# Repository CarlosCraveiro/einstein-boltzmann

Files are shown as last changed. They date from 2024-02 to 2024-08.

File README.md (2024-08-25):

# The Einstein-Boltzmann Board

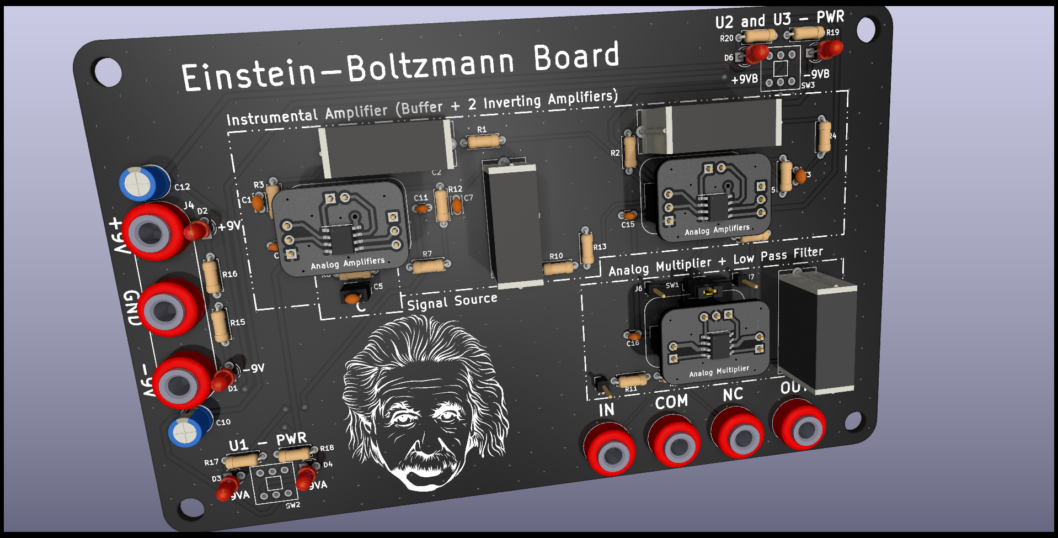
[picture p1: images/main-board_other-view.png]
main_board_other_view


## Project's Intent
Measure the Boltzmann constant through the analysis of the thermal noise of a resistor.

## Disclaimer
This Board was intended to be used with the Guide of the [5-th EPO (2017)](https://github.com/CarlosCraveiro/einstein-boltzmann/tree/main/docs).

So the schematic ideia is not mine, I just adapt and documented it so I could manufacture the board.

The DRC Custom Rules used on this project came from a gist made by [darkxst](https://gist.github.com/darkxst), Gist name: `rules.txt`.

## Project's Dependencies

- KiCAD version 7.0
- KiCAD Addon [kicad-action-scripts](https://github.com/jsreynaud/kicad-action-scripts) (via stitching)

If you use `nix`, to have access to **KiCAD 7.0**, on the project's directory type:

```shell
nix --experimental-features 'nix-command flakes'
nix develop -c $SHELL
```

## Preview Images

### Main Board
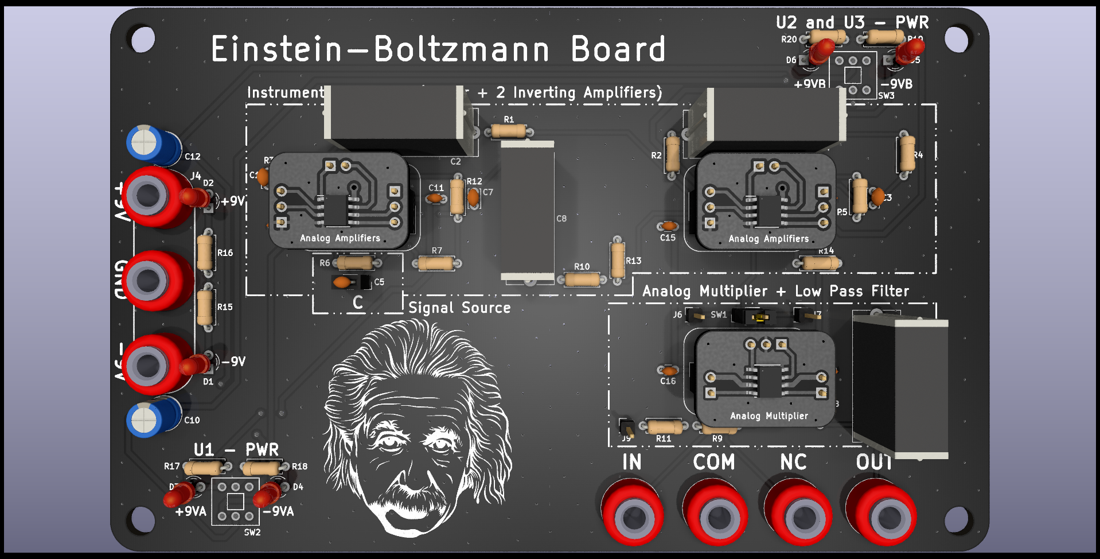
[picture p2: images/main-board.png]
main_board_front

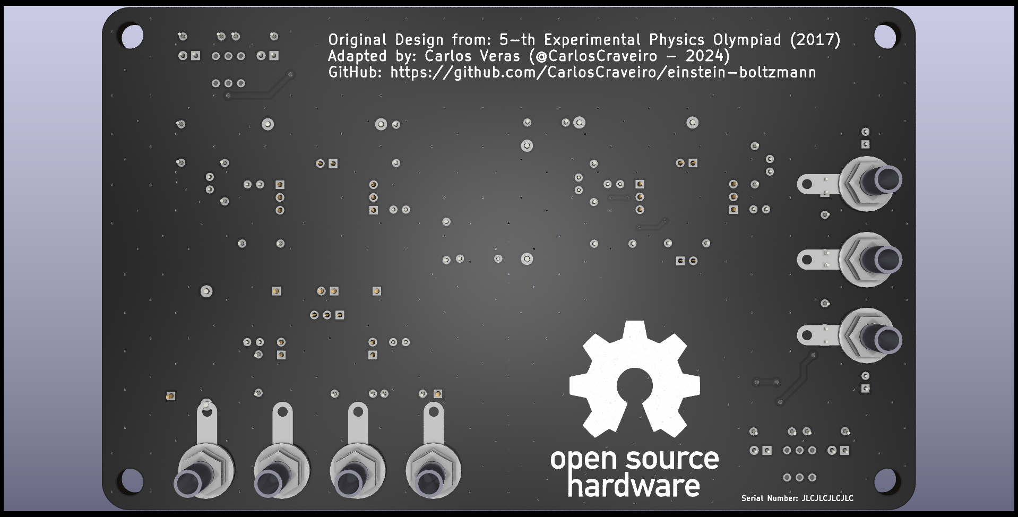
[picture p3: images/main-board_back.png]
main_board_back


### Modules
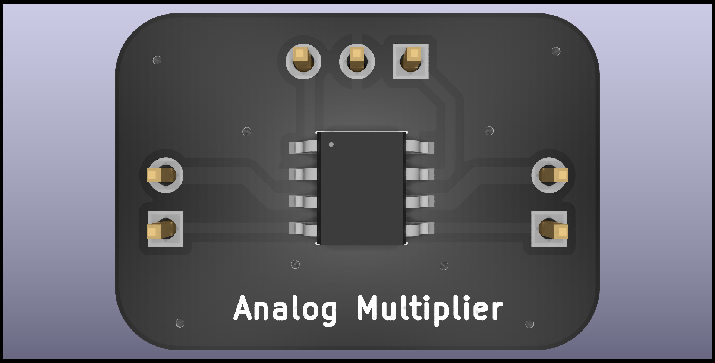
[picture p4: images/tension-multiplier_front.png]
tension-multiplier_front

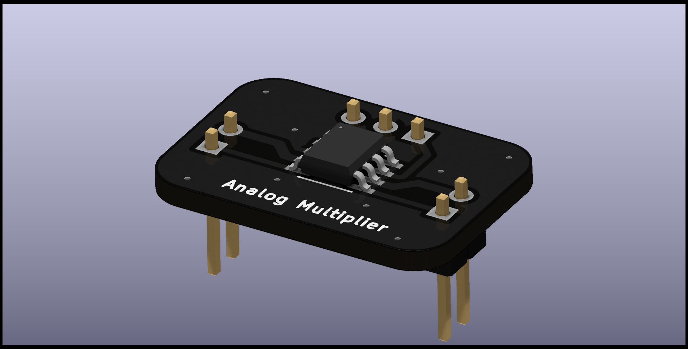
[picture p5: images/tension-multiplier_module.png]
tension-multiplier_module

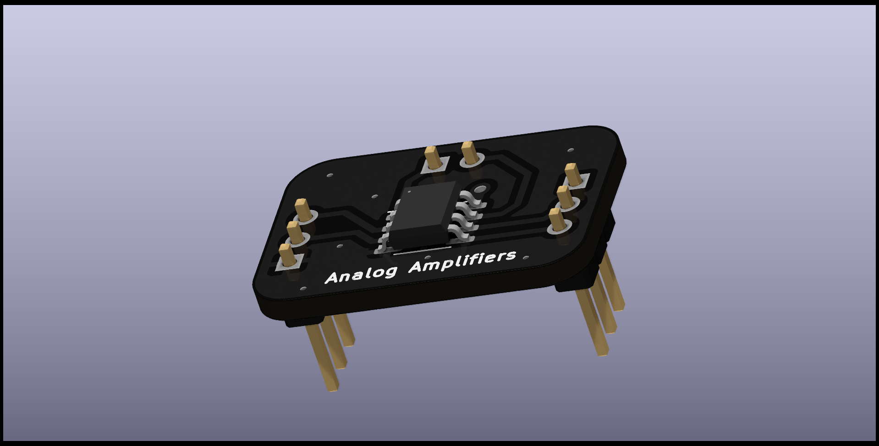
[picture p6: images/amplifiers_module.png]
amplifiers_module

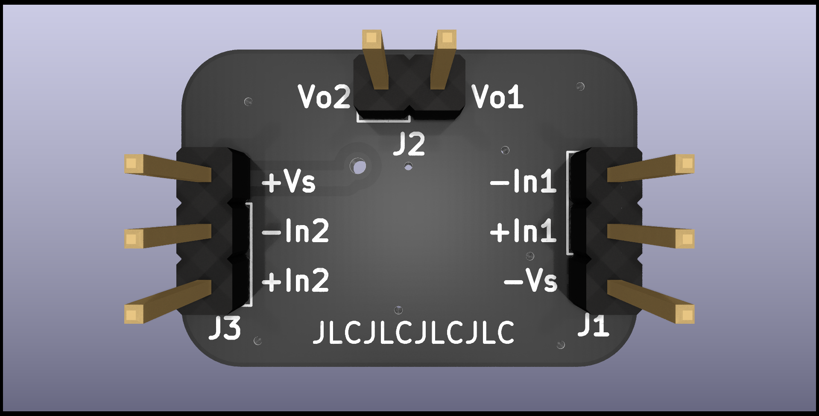
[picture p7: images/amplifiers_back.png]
amplifiers_back


## Real Photos
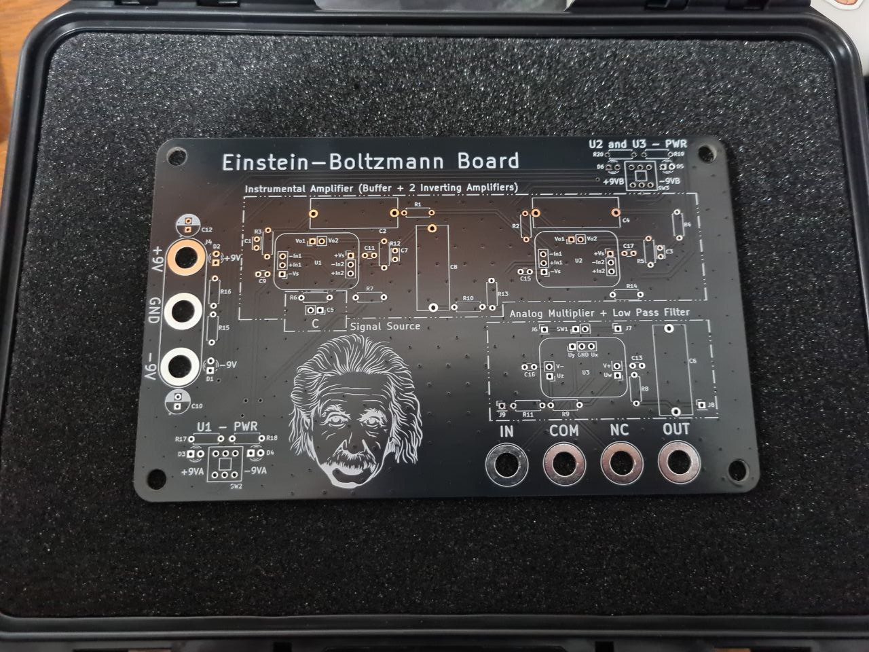
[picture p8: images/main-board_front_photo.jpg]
main-board_front

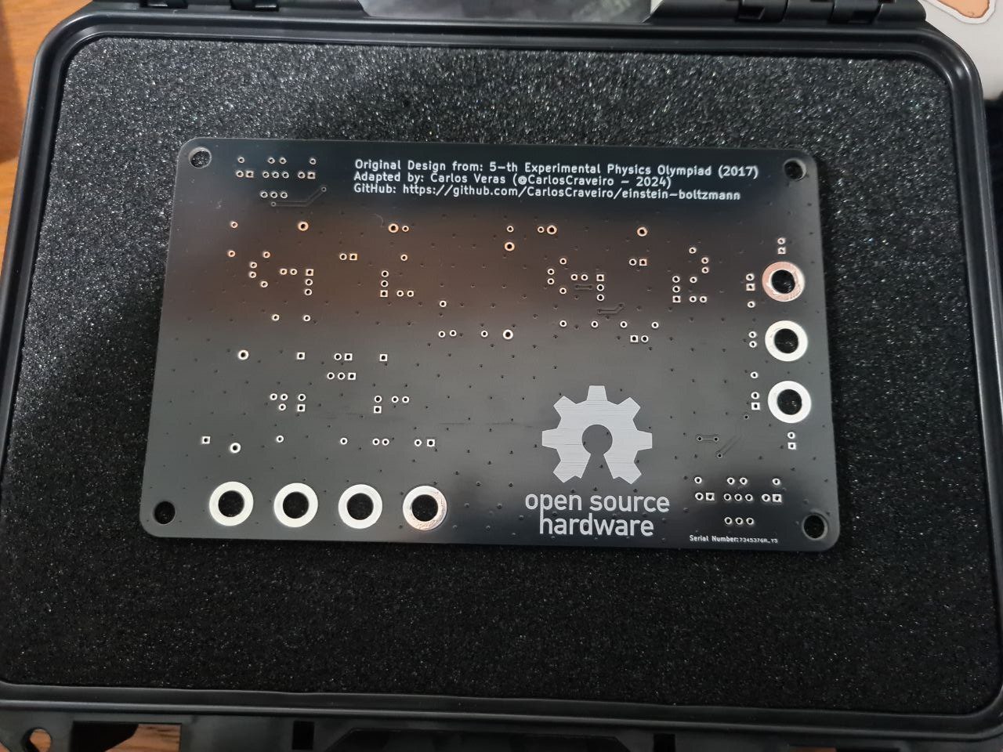
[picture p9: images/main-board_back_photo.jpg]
main-board_back


## TO DO...
- [ ]  Finish soldering the components and modules
- [ ]  Create a Wiki for the project
- [ ]  Measure the Boltzmann constant and publish the results on the project's Wiki
- [ ]  Finish the plate support base (using FreeCAD)
- [ ]  Write a theoretical introduction about the phenomenon on the project's Wiki

*Observation*: I intend to continue working on the project, I just need time.

## Additional information:

I talked about the project at the [FOSFORUMS 2024](https://www.fosforums.org/home) event. The presentation were in English and both the slides and the link for the presentation recording could be access [here](https://github.com/CarlosCraveiro/FOSFORUMS_2024).

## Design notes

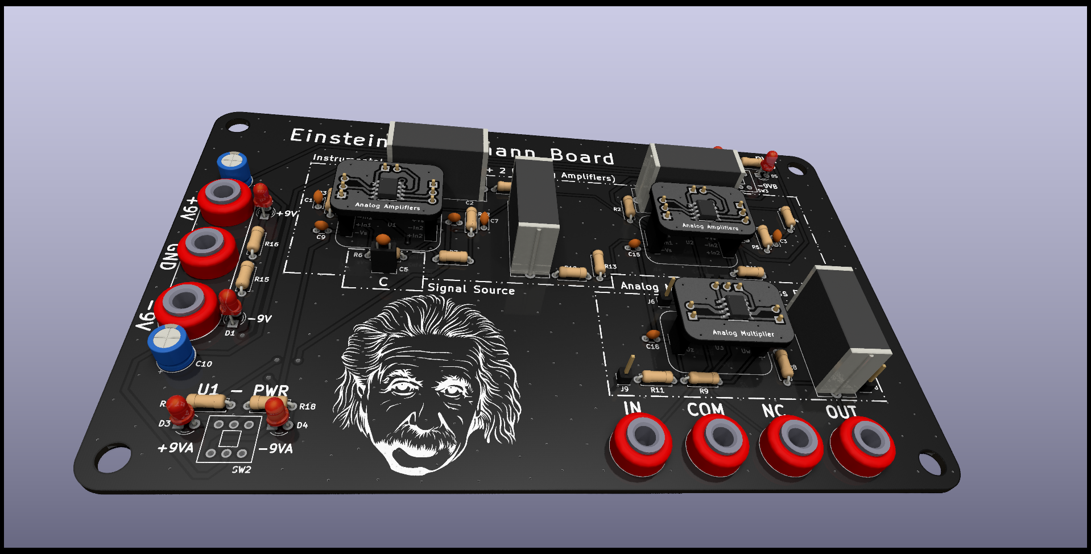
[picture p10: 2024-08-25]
images/main-board_modules_view.png

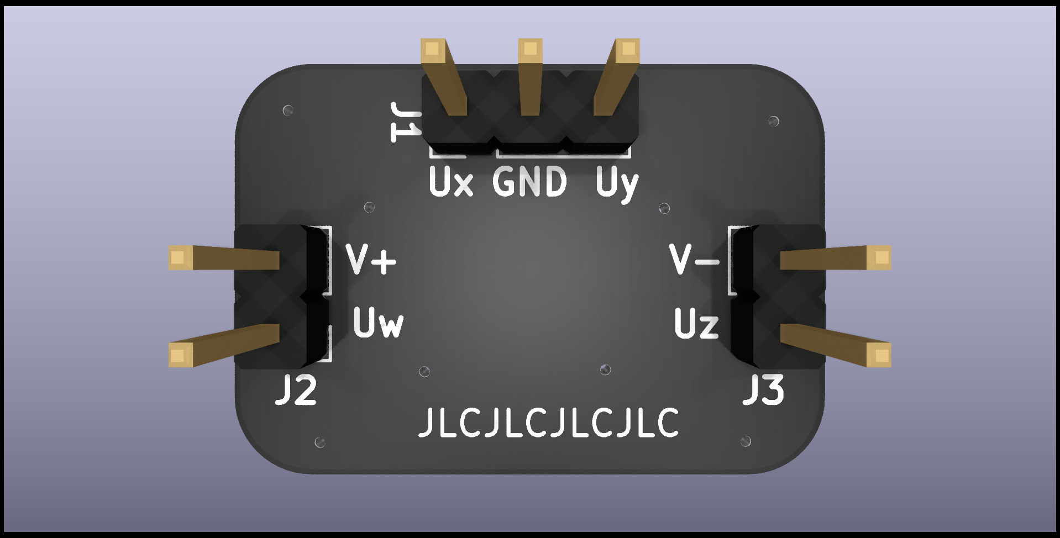
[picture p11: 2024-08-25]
images/tension-multiplier_back.png

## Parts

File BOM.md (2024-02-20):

# BOM - Bill of Materials

## Main Board

|                           |       |
| ------------------------- | ----- |
| Qty of Boards per project | **1** |

* Capacitors: 

| Components               | Qty   |  Unit Price (BRL) | Link                                                                                                      | Link 2 |
| ------------------------ | ----- | ----------------- | --------------------------------------------------------------------------------------------------------- | ------ |
| EC Capacitor 10uF        | **4** | 0.15 / 0.15       | [Bau da Eletronica](https://www.baudaeletronica.com.br/produto/capacitor-eletrolitico-10uf-25v-105c.html) | [Saravati](https://www.saravati.com.br/capacitor-eletrolitico-10uf-16v.html) |
| Tantalum Capacitor 0.1uF | **4** | 0.99              | [Bau da Eletronica](https://www.baudaeletronica.com.br/produto/capacitor-tantalo-01uf-35v.html)           ||
| Tantalum Capacitor 10uF  | **4** | 0.92              | [Bau da Eletronica](https://www.baudaeletronica.com.br/produto/capacitor-tantalo-10uf-16v.html)           ||
| Ceramic Capacitor 10pF   | **3** | 0.17 / 0.10       | [Bau da Eletronica](https://www.baudaeletronica.com.br/produto/capacitor-ceramico-10pf-50v.html)          | [Saravati](https://www.saravati.com.br/capacitor-ceramico-10pf-50v.html) |

* Resistors:

| Components        | Qty   | Unit Price (BRL) | Link                                                                                     | Link 2 |
| ----------------- | ----- | ---------------- | ---------------------------------------------------------------------------------------- | ------ |
| Resistor 510 Ohm  | **1** | 0.05             | [Baú da Eletrônica](https://www.baudaeletronica.com.br/produto/resistor-510r-5-14w.html) | [AliExpress]() |
| Resistor 20 Ohm   | **1** | 0.05 / 0.09      | [Baú da Eletrônica](https://www.baudaeletronica.com.br/produto/resistor-20r-5-14w.html)  | [Saravati](https://www.saravati.com.br/resistor-20r-5-1-4w.html) |
| Resistor 1k Ohm   | **2** | 0.05 / 0.09      | [Baú da Eletrônica](https://www.baudaeletronica.com.br/produto/resistor-1k-5-14w.html)   | [Saravati](https://www.saravati.com.br/resistor-1k-5-1-4w.html) |
| Resistor 100 Ohm  | **4** | 0.04 / 0.09      | [Baú da Eletrônica](https://www.baudaeletronica.com.br/produto/resistor-100r-5-14w.html) | [Saravati](https://www.saravati.com.br/resistor-100r-5-1-4w.html) |
| Resistor 10k Ohm  | **3** | 0.05 / 0.09      | [Baú da Eletrônica](https://www.baudaeletronica.com.br/produto/resistor-10k-5-14w.html)  | [Saravati](https://www.saravati.com.br/resistor-10k-5-1-4w.html) |
| Resistor 1.5M Ohm | **1** | 0.05             | [Baú da Eletrônica](https://www.baudaeletronica.com.br/produto/resistor-1m5-5-14w.html)  | []() |
| Resistor 18k Ohm  | **1** | 0.05             | [Baú da Eletrônica](https://www.baudaeletronica.com.br/produto/resistor-18k-5-14w.html)  | []() |
| Resistor 2k Ohm   | **5** | 0.05             | [Baú da Eletrônica](https://www.baudaeletronica.com.br/produto/resistor-2k-5-14w.html)   | []() |

* LEDs:

| Components | Qty   | Unit Price (BRL) | Link                                                                                     | Link 2 |
| ---------- | ----- | ---------------- | ---------------------------------------------------------------------------------------- | ------ |
| LED 3mm    | **4** | 0.24 / 0.20      | [Bau da Eletronica](https://www.baudaeletronica.com.br/produto/led-difuso-3mm-azul.html) | [Saravati](https://www.saravati.com.br/led-difuso-3mm-azul.html) |

* Pin-Headers:

| Components            | Qty    | Bar Price (BRL) | Link                                                                                               |
| --------------------- | ------ | --------------- | -------------------------------------------------------------------------------------------------- |
| 1x01-P2.54mm_Vertical | **10** | 1.50            | [Saravati](https://www.saravati.com.br/barra-de-pinos-1x40-vias-8-2mm-180-graus-passo-2-54mm.html) |

* Pin-Sockets:

| Components            | Qty   | Bar Price (BRL) | Link                                                                                                |
| --------------------- | ----- | --------------- | --------------------------------------------------------------------------------------------------- |
| 1x03_P2.54mm_Vertical | **5** | 1.90            | [Saravati](https://www.saravati.com.br/soquete-barra-de-pinos-1x40-mci-180-graus-passo-2-54mm.html) |
| 1x02_P2.54mm_Vertical | **4** | 1.90            | [Saravati](https://www.saravati.com.br/soquete-barra-de-pinos-1x40-mci-180-graus-passo-2-54mm.html) |

* Other:

| Components               | Qty   | Unit Price (BRL) | Link                                                                                              | Link 2  |
| ------------------------ | ----- | ---------------- | ------------------------------------------------------------------------------------------------- | ------- |
| Mini-Jumper_1x02_P2.54mm | **1** | 0.15 / 0.15      | [Bau da Eletronica](https://www.baudaeletronica.com.br/produto/conector-mini-jumper-sem-aba.html) | [Saravati](https://www.saravati.com.br/jumper-fecha-contato-preto.html) |

## Analog Amplifiers Board

|                           |       |
| ------------------------- | ----- |
| Qty of Boards per project | **2** |

* Pin-Headers:

| Components            | Qty   |
| --------------------- | ----- |
| 1x03_P2.54mm_Vertical | **2** |
| 1x02_P2.54mm_Vertical | **1** |

* ICs: 

| Components    | Qty   |
| ------------- | ----- |
| ADA4898-2YRDZ | **1** | 

## Analog Multiplier Board

|                           |       |
| ------------------------- | ----- |
| Qty of Boards per project | **1** |

* Pin-Headers:

| Components            | Qty   |
| --------------------- | ----- |
| 1x03_P2.54mm_Vertical | **1** |
| 1x02_P2.54mm_Vertical | **2** |

* ICs: 

| Components | Qty   |
| ---------- | ----- |
| AD633ARZ   | **1** | 

## Experience Components

* Capacitors:

| Components                 | Qty   | Unit Price (BRL) | Link                                                                                             | Link 2    |
| -------------------------- | ----- | ---------------- | ------------------------------------------------------------------------------------------------ | --------- |
| *Ceramic Capacitor 6.8nF*  | **1** | 0.10             | [Saravati](https://www.saravati.com.br/capacitor-ceramico-6-8nf-50v.html)                        |           |
| *Ceramic Capacitor 10.3nF* | **1** | 0.10             | [Saravati](https://www.saravati.com.br/capacitor-ceramico-10nf-50v.html)                         |           |
| Ceramic Capacitor 14.8nF   | **1** | 0.10 / 0.10      | [Baú da Eletrônica](https://www.baudaeletronica.com.br/produto/capacitor-ceramico-15nf-50v.html) | [Saravati](https://www.saravati.com.br/capacitor-ceramico-15nf-50v.html) |
| *Ceramic Capacitor 20.3nF* | **1** | 0.58             | [Baú da Eletrônica](https://www.baudaeletronica.com.br/produto/capacitor-ceramico-20nf-50v.html) |           |
| *Ceramic Capacitor 22.3nF* | **1** | 0.10             | [Saravati](https://www.saravati.com.br/capacitor-ceramico-22nf-50v.html)                         |           |
| Ceramic Capacitor 27.9nF   | **1** | 0.55             | [CaAndMa](https://caandma.com.br/)                                                               |           |
| Ceramic Capacitor 33.4nF   | **1** | 0.14 / 0.10      | [Baú da Eletrônica](https://www.baudaeletronica.com.br/produto/capacitor-ceramico-33nf-50v.html) | [Saravati](https://www.saravati.com.br/capacitor-ceramico-15nf-50v.html) |
| Ceramic Capacitor 42.3nF   | **1** | 0.10             | [Saravati](https://www.saravati.com.br/capacitor-ceramico-47nf-50v.html)                         |           |
| Ceramic Capacitor 66.9nF   | **1** | 0.10             | [Saravati](https://www.saravati.com.br/capacitor-ceramico-68nf-50v.html)                         |           |
| Ceramic Capacitor 105nF    | **1** | 0.10             | [Saravati](https://www.saravati.com.br/capacitor-ceramico-100nf-50v.html)                        |           |

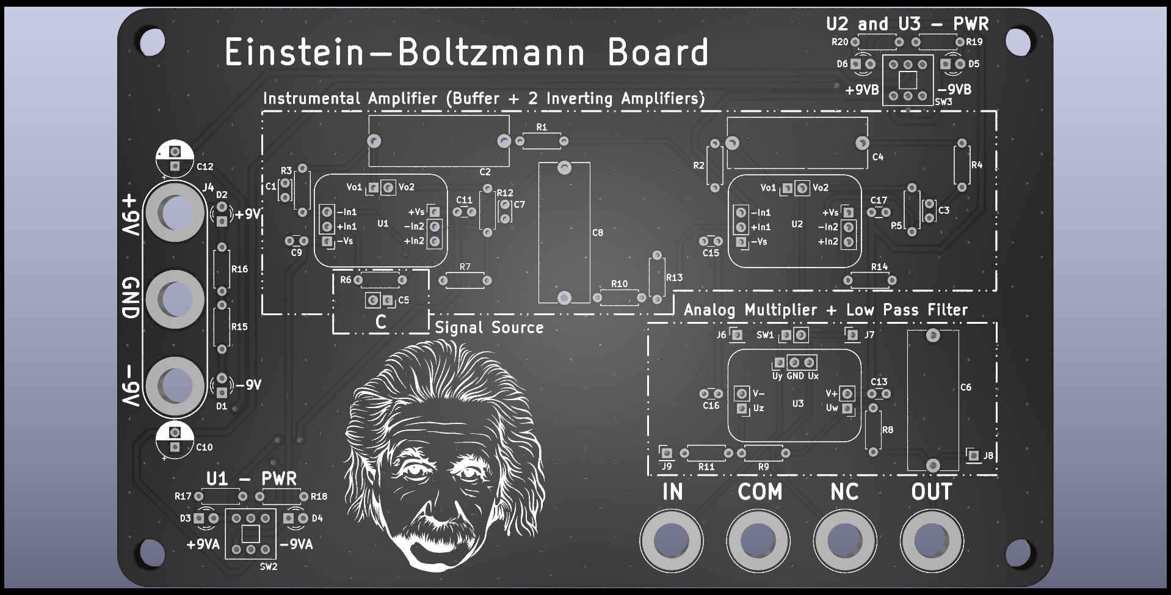
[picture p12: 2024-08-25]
images/main-board_front_no_components.png

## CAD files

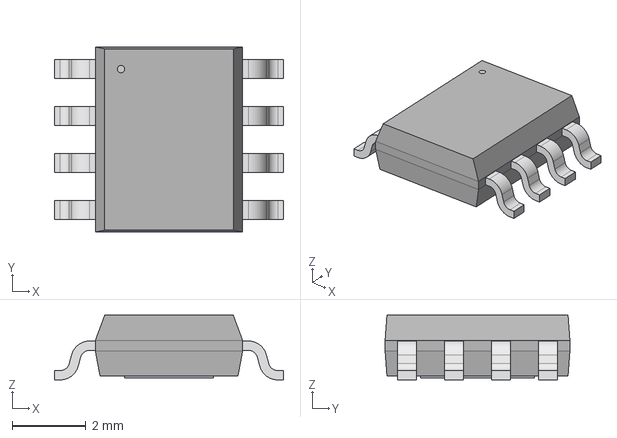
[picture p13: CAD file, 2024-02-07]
amplifiers/RD_8_2_ADI.step
6.20 x 5.00 x 1.75 mm

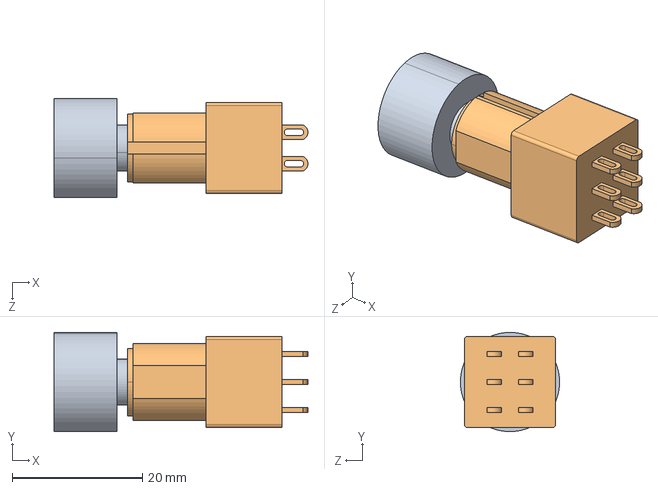
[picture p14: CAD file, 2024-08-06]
main-board/module_3Dmodels/DPDT.step
39.0 x 15.2 x 15.2 mm
MPG206R(2)
MPG206R(1)

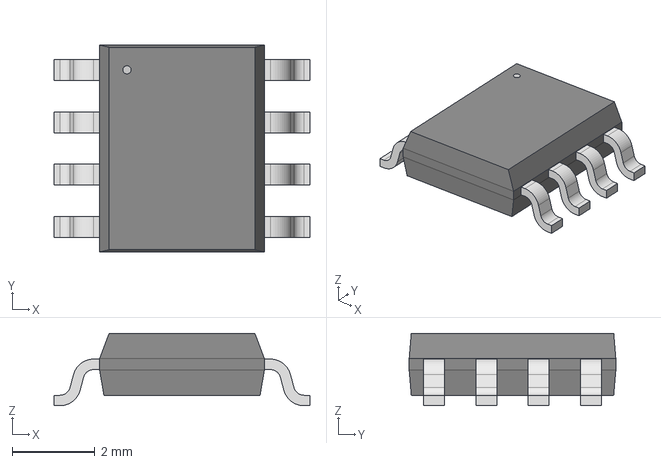
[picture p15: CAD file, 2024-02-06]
tension-multiplier/R_8_ADI.step
6.20 x 5.00 x 1.75 mm

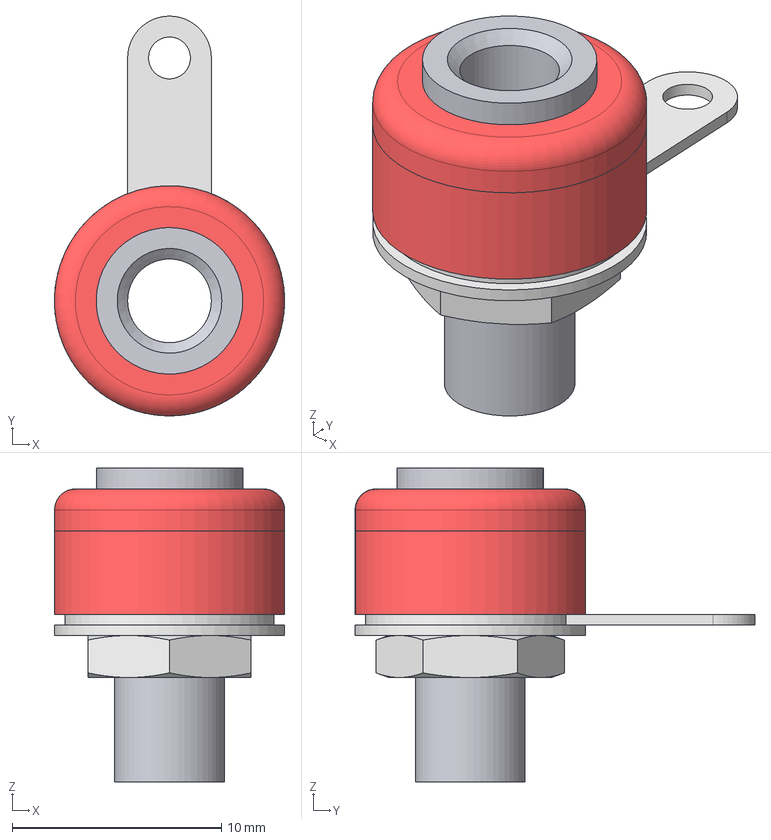
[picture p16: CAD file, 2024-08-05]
main-board/module_3Dmodels/4mm Panel Mount Banana Socket.stp
11.0 x 19.1 x 15.0 mm
Plastic Cap
Plastic Cap top
Socket Tube
Wire Connector
Washer
Connector Nut

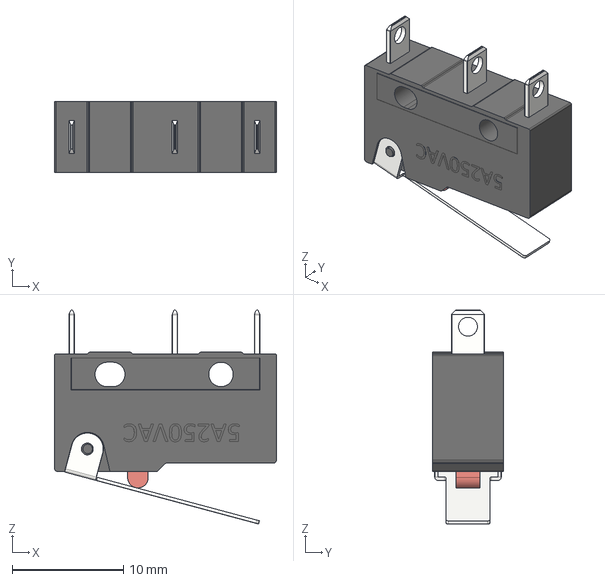
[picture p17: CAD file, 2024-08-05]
main-board/module_3Dmodels/microswith.step
20.0 x 6.44 x 19.3 mm

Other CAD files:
mounting-base/mountingbase.FCStd
amplifiers/RD_8_2_ADI.stl
tension-multiplier/R_8_ADI.stl

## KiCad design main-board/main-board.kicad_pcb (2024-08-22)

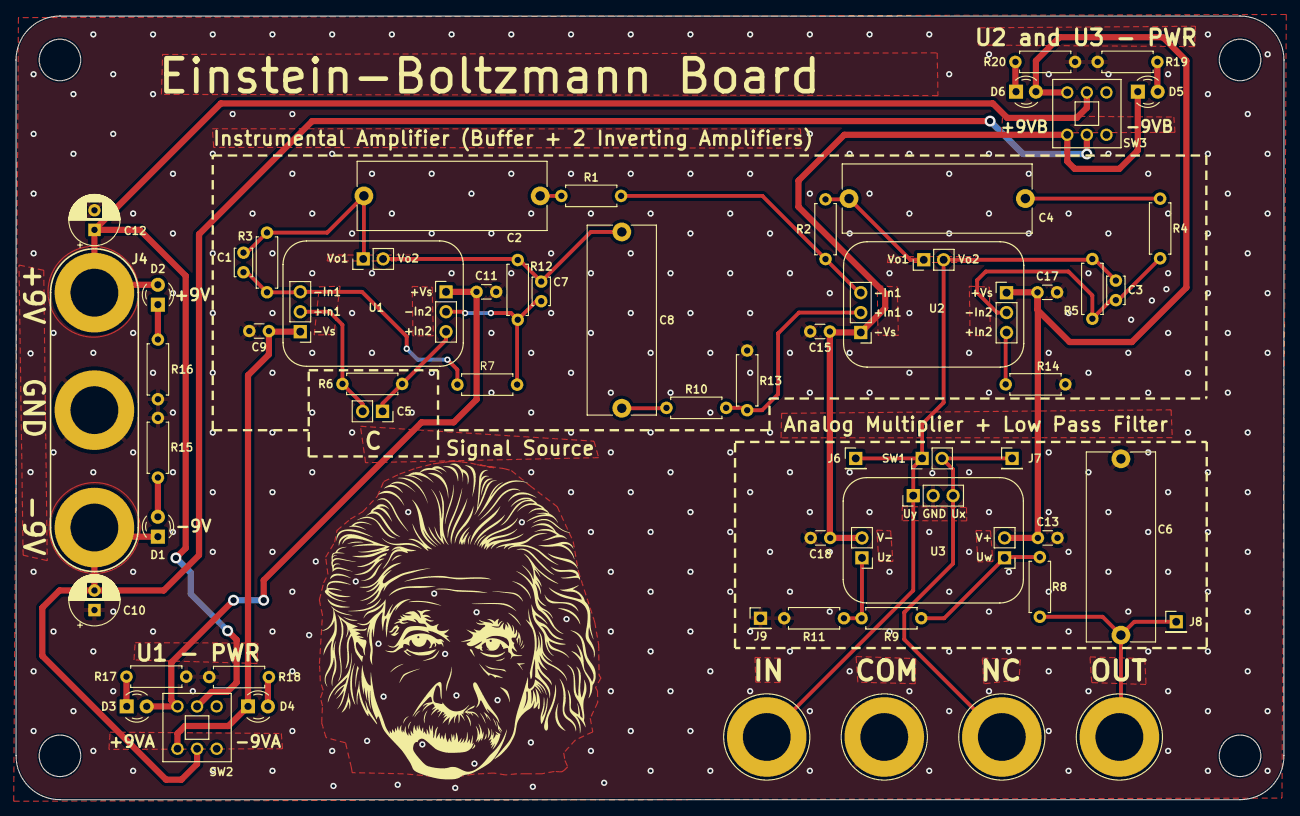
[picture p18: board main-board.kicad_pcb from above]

Board: 2 copper layers, 161.8 x 100.0 mm, 61 parts (0 on the bottom side), 32 nets.

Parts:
C1, C3, C7: 10p; C_Disc_D3.4mm_W2.1mm_P2.50mm
C2, C4, C6, C8: 10u; C_Rect_L24.0mm_W8.6mm_P22.50mm_MKT
C5: c=?; CapacitorSocket
C9, C11, C13, C15, C17, C18: 0.1u; C_Disc_D3.0mm_W1.6mm_P2.50mm
C10, C12: 10u; CP_Radial_D6.3mm_P2.50mm
D1, D2, D3, D4, D5, D6: LED; LED_D3.0mm
H1, H2, H3, H4: MountingHole; MountingHole_5.3mm_M5
J1: INPUT; Banana_Jack_1Pin
J2: NC1; Banana_Jack_1Pin
J3: OUTPUT; Banana_Jack_1Pin
J4: Conn_01x03_Pin; Banana_Jack_3Pin
J5: COM; Banana_Jack_1Pin
J6: INPUT_DEBUG; PinHeader_1x01_P2.54mm_Vertical
J7: NC__DEBUG; PinHeader_1x01_P2.54mm_Vertical
J8: OUTPUT_DEBUG; PinHeader_1x01_P2.54mm_Vertical
J9: COM_DEBUG; PinHeader_1x01_P2.54mm_Vertical
R1, R4, R10, R14: 100; R_Axial_DIN0207_L6.3mm_D2.5mm_P7.62mm_Horizontal
R2, R5, R13: 10k; R_Axial_DIN0207_L6.3mm_D2.5mm_P7.62mm_Horizontal
R3, R12: 1k; R_Axial_DIN0207_L6.3mm_D2.5mm_P7.62mm_Horizontal
R6: 510; R_Axial_DIN0207_L6.3mm_D2.5mm_P7.62mm_Horizontal
R7: 20; R_Axial_DIN0207_L6.3mm_D2.5mm_P7.62mm_Horizontal
R8: 1.5M; R_Axial_DIN0207_L6.3mm_D2.5mm_P7.62mm_Horizontal
R9, R15, R16, R17, R18, R19, R20: 2k; R_Axial_DIN0207_L6.3mm_D2.5mm_P7.62mm_Horizontal
R11: 18k; R_Axial_DIN0207_L6.3mm_D2.5mm_P7.62mm_Horizontal
SW1: SW_SPST; Switch
SW2: Power Switch A; SW_Push_2P2T_Toggle_CK_PSW-8,0R
SW3: Power Switch B; SW_Push_2P2T_Toggle_CK_PSW-8,0R
U1, U2: ADA4898-2
U3: AD633ANZ; AD633

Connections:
+9V: C12.1, D2.2 (A), J4.1, SW2.2 (B), SW3.2 (B)
+9VA: C11.1, D3.2 (A), SW2.1 (A), U1.6 (+Vs)
+9VB: C13.1, C17.1, D6.2 (A), SW3.1 (A), U2.6 (+Vs), U3.6 (V+)
-9V: C10.2, D1.1 (K), J4.3, SW2.5 (B), SW3.5 (B)
-9VA: C9.1, D4.1 (K), SW2.4 (A), U1.1 (-Vs)
-9VB: C15.1, C18.1, D5.1 (K), SW3.4 (A), U2.1 (-Vs), U3.2 (V-)
/led_+9V: D2.1 (K), R16.1
/led_+9VA: D3.1 (K), R17.1
/led_+9VB: D6.1 (K), R20.1
/led_-9V: D1.2 (A), R15.1
/led_-9VA: D4.2 (A), R18.1
/led_-9VB: D5.2 (A), R19.1
/w1: C1.1, R3.1, R7.1, U1.3 (-In1)
/w2: C7.1, R7.2, R12.2, U1.7 (-In2)
/w3: C1.2, C2.1, R3.2, U1.4 (Vo1)
/w4: C7.2, C8.1, R12.1, U1.5 (Vo2)
/w5: C2.2, R1.1
/w6: C8.2, R10.1
/w7: R1.2, R2.1, U2.3 (-In1)
/w8: R10.2, R13.2, U2.2 (+In1)
/w9: R14.2, U2.8 (+In2)
/w10: C4.1, R2.2, U2.4 (Vo1)
/w11: C4.2, R4.1
/w12: C3.1, R4.2, R5.1, U2.7 (-In2)
/w13: R8.1, R9.1, U3.7 (Uw)
/w14: R9.2, R11.1, U3.1 (Uz)
/w_input: C3.2, J1.1, J6.1, R5.2, SW1.1 (A), U2.5 (Vo2), U3.3 (Uy)
/w_nc: J2.1, J7.1, SW1.2 (B), U3.5 (Ux)
/w_out: C6.1, J3.1, J8.1, R8.2
/w_signal+: C5.2, R6.1, U1.2 (+In1)
/w_signal-: C5.1, R6.2, U1.8 (+In2)
GND: C6.2, C9.2, C10.1, C11.2, C12.2, C13.2, C15.2, C17.2, C18.2, J4.2, J5.1, J9.1, R11.2, R13.1, R14.1, R15.2, R16.2, R17.2, R18.2, R19.2, R20.2, U3.4 (GND)

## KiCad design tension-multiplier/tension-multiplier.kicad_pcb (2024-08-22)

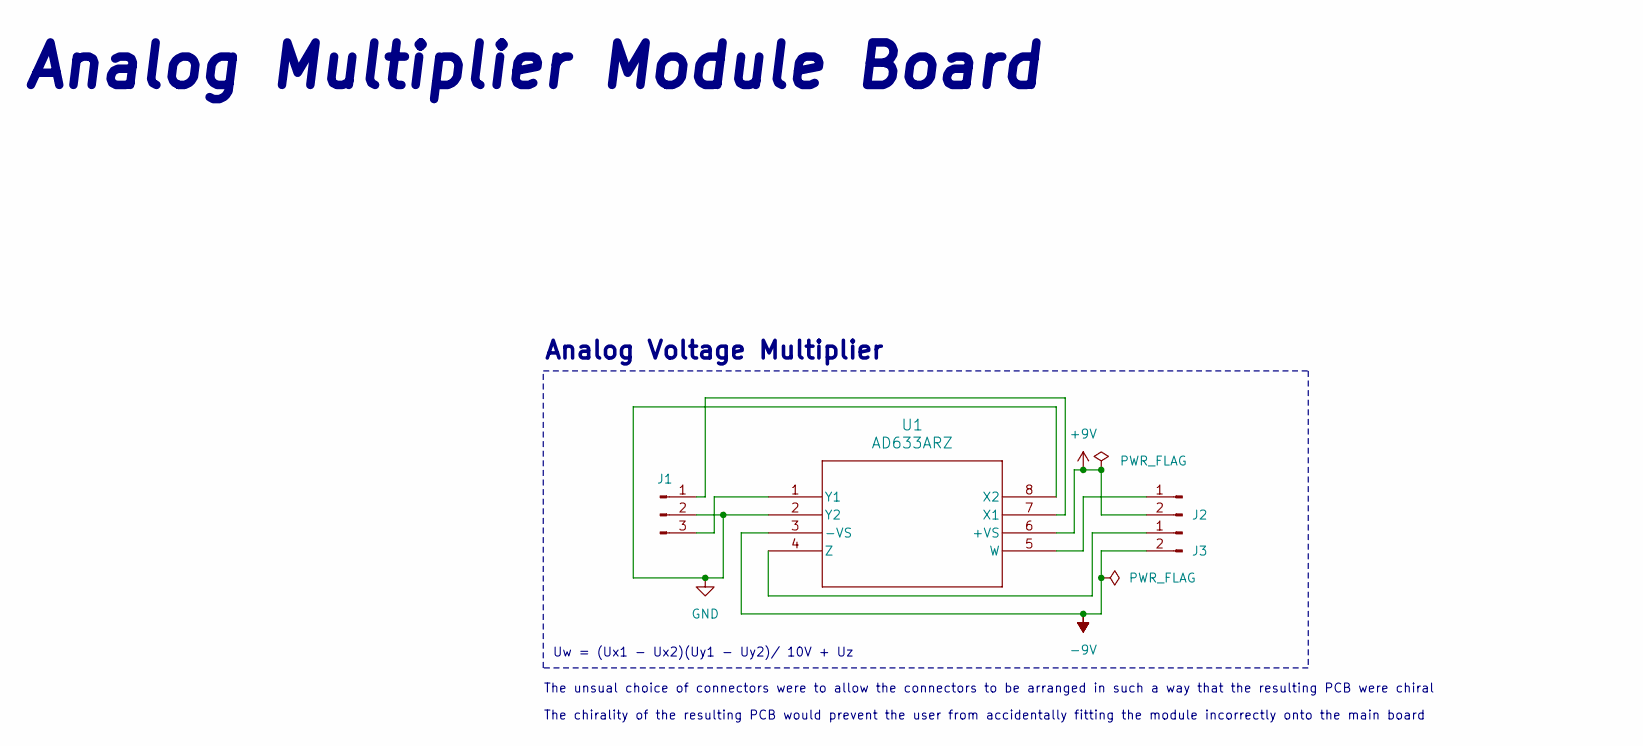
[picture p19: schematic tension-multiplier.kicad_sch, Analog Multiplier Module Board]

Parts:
J1: Conn_01x03_Pin; PinHeader_1x03_P2.54mm_Vertical
J2, J3: Conn_01x02_Pin; PinHeader_1x02_P2.54mm_Vertical
U1: AD633ARZ; R_8_ADI

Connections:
+9V: J2.2, U1.6 (+VS)
-9V: J3.2, U1.3 (-VS)
GND: J1.2, U1.2 (Y2), U1.8 (X2)
unnamed: J1.1, U1.7 (X1)
unnamed: J1.3, U1.1 (Y1)
unnamed: J2.1, U1.5 (W)
unnamed: J3.1, U1.4 (Z)

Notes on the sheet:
The chirality of the resulting PCB would prevent the user from accidentally fitting the module incorrectly onto the main board
Analog Multiplier Module Board
Analog Voltage Multiplier
The unsual choice of connectors were to allow the connectors to be arranged in such a way that the resulting PCB were chiral
Uw = (Ux1 - Ux2)(Uy1 - Uy2)/ 10V + Uz

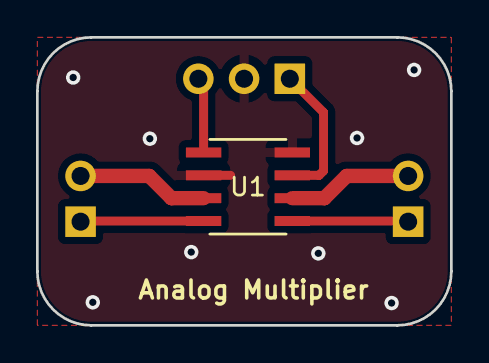
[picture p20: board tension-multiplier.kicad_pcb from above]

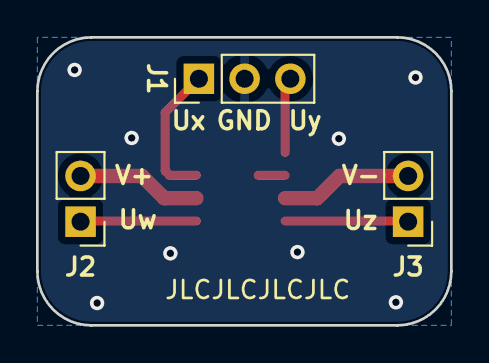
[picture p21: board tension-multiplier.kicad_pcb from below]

Board: 2 copper layers, 23.0 x 16.0 mm, 4 parts (3 on the bottom side), 7 nets.

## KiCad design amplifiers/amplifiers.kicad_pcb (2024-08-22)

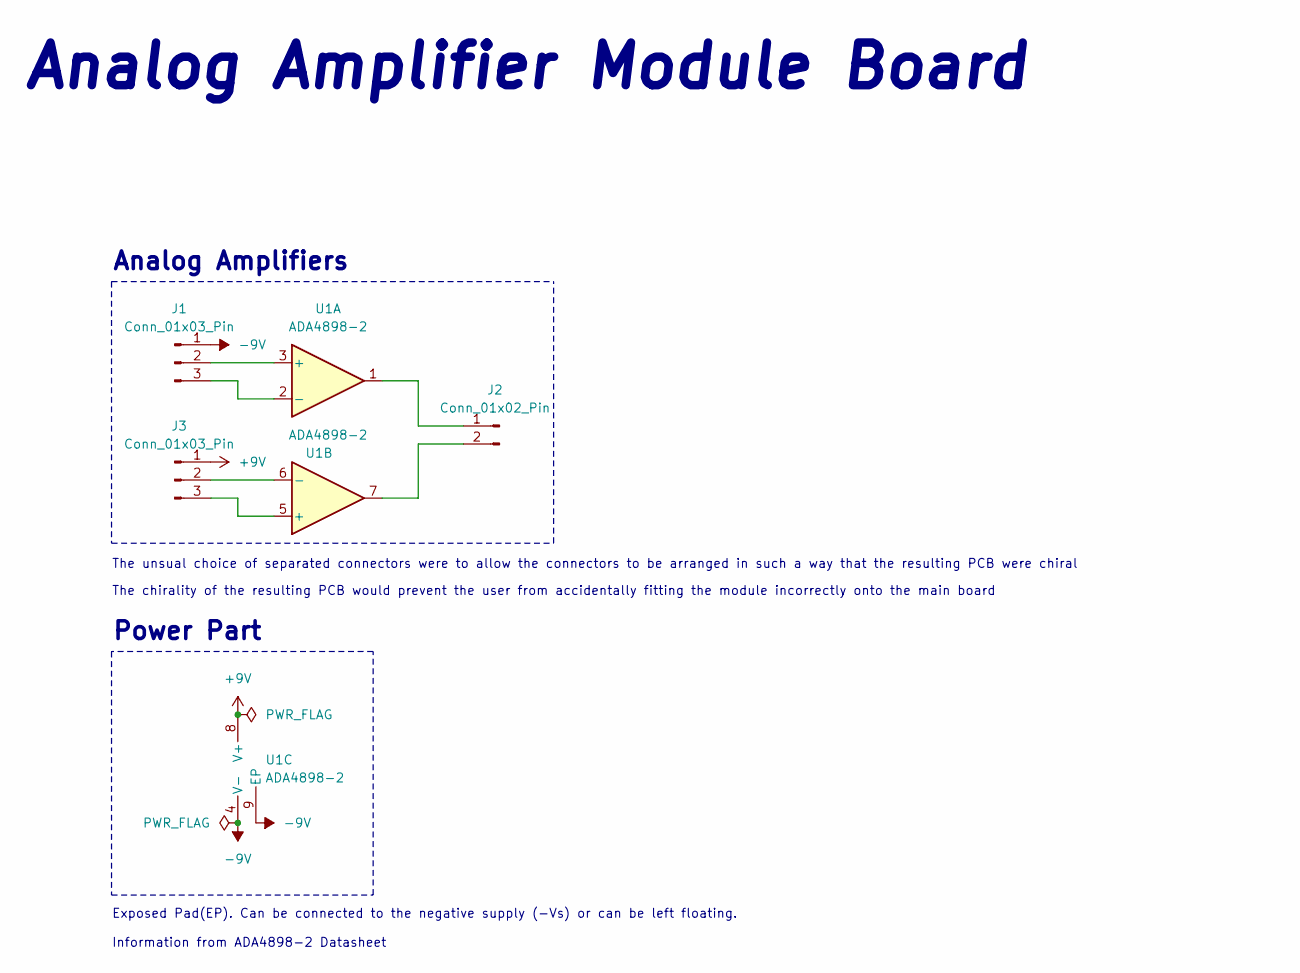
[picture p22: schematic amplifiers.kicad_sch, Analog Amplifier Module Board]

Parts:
J1, J3: Conn_01x03_Pin; PinHeader_1x03_P2.54mm_Vertical
J2: Conn_01x02_Pin; PinHeader_1x02_P2.54mm_Vertical
U1: ADA4898-2; SOIC-8-1EP_3.9x4.9mm_P1.27mm_EP2.41x3.81mm

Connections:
+9V: J3.1, U1.8 (V+)
-9V: J1.1, U1.4 (V-), U1.9 (EP)
unnamed: J1.2, U1.3 (+)
unnamed: J1.3, U1.2 (-)
unnamed: J2.1, U1.1
unnamed: J2.2, U1.7
unnamed: J3.2, U1.6 (-)
unnamed: J3.3, U1.5 (+)

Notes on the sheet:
Power Part
The unsual choice of separated connectors were to allow the connectors to be arranged in such a way that the resulting PCB were chiral
Exposed Pad(EP). Can be connected to the negative supply (−Vs) or can be left floating. Information from ADA4898-2 Datasheet
Analog Amplifier Module Board
Analog Amplifiers
The chirality of the resulting PCB would prevent the user from accidentally fitting the module incorrectly onto the main board

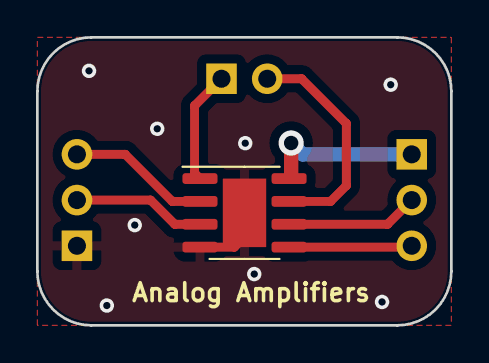
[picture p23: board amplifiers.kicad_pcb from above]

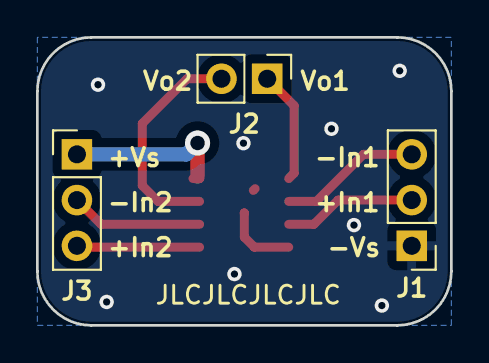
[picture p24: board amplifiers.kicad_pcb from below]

Board: 2 copper layers, 23.0 x 16.0 mm, 4 parts (3 on the bottom side), 8 nets.

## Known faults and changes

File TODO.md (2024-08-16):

# Project's TO-DO List:

- [ ] Write the Board's Instruction Manual

- [ ] Write Project's README and Wiki

- [ ] Upload the EPO Test pdf on Github

- [ ] Update, Complete and Improves project's BOM

- [ ] Finish the Mounting Base

- [ ] Improve the Simulation

- [ ] Improve project's organization

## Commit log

2024-02-06 creates main board project
    [main-board.kicad_pcb, main-board.kicad_sch]
2024-02-06 creates amplifiers project
    [amplifiers.kicad_pcb, amplifiers.kicad_sch]
2024-02-06 creates tension-multiplier project
    [tension-multiplier.kicad_pcb, tension-multiplier.kicad_sch]
2024-02-06 Finishes version 0.1 of the analog multiplier schematic
    [tension-multiplier.kicad_sch]
2024-02-06 Starts PCB layout for analog multiplier
    [R_8_ADI.step, R_8_ADI.stl, tension-multiplier.kicad_pcb, tension-multiplier.kicad_sch]
2024-02-07 Finishes version 0.1 of Analog Multiplier Module
    [tension-multiplier.kicad_pcb]
2024-02-07 start design of Amplifier module boards
    [amplifiers.kicad_pcb, amplifiers.kicad_sch]
2024-02-07 Finishes version 0.1 of amplifier module board
    [RD_8_2_ADI.step, RD_8_2_ADI.stl, amplifiers.kicad_pcb, amplifiers.kicad_sch]
2024-02-08 Starts the Main Board design
    [main-board.kicad_sch]
2024-02-11 Adds a working Simulation
    [simulation.kicad_pcb, simulation.kicad_sch]
2024-02-11 Adds some flootprints to the main board
    [main-board.kicad_sch]
2024-02-12 Selects all footprints to the main board schematics
    [main-board.kicad_pcb, main-board.kicad_sch]
2024-02-13 Adjust main board footprints and pcb layout
    [Jumper.step, main-board.kicad_pcb, main-board.kicad_sch]
2024-02-13 Modifies PCB Layout cosmetics
    [main-board.kicad_pcb, main-board.kicad_sch]
2024-02-13 Changes dimentions of the tension multiplier
    [tension-multiplier.kicad_pcb]
2024-02-14 Refactors modules pcblayout to cosmetic purposes
    Also, refactors Amplifiers moduleboard to include a VEE plane
    (powerplane).
    [amplifiers.kicad_pcb, tension-multiplier.kicad_pcb]
2024-02-14 Changes 3d files and footprints to match module cosmetic changes
    [main-board.kicad_pcb]
2024-02-14 Modifies Main Board PCB Layout component disposal
    [main-board.kicad_pcb, main-board.kicad_sch]
2024-02-14 Modifies main board layout components displacement
    [main-board.kicad_pcb]
2024-02-14 Starts routing the main board
    [main-board.kicad_pcb]
2024-02-15 Finishes version Beta of the project
    [main-board.kicad_pcb]
2024-02-15 Starts Pannelization
    [pannel.kicad_pcb, pannel.kicad_sch]
2024-02-16 test gerber files and add JLC serial number to the main board
    [main-board-B_Cu.gbr, main-board-B_Mask.gbr, main-board-B_Paste.gbr, main-board-B_Silkscreen.gbr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]
2024-02-16 Starts the Bill of Materials of the project
2024-02-16 Add JLCPCB serial number to the module pcbs
    [amplifiers.kicad_pcb, tension-multiplier.kicad_pcb]
2024-02-16 Give up from the idea from pannelization
    [pannel.kicad_pcb, pannel.kicad_sch]
2024-02-17 Add Capacitor Prices
2024-02-17 Add LED price
2024-02-17 Add resistor prices
2024-02-17 add capacitor price incomplete
2024-02-17 Adds capacitor and pin headers and socket prices
2024-02-21 Starts design of mounting base
    [mountingbase.FCStd]
2024-02-21 Change M8 Holes to M5 Holes
    [main-board.kicad_pcb, main-board.kicad_sch]
2024-08-04 Changes capacitor and resistor footprints
    [main-board.kicad_pcb, main-board.kicad_sch]
2024-08-05 Saves progress
    [4mm Panel Mount Banana Socket.stl, 4mm Panel Mount Banana Socket.stp, main-board.kicad_pcb, main-board.kicad_sch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]
2024-08-06 Adds Switch footprint and 3d model
    [SPDT_slide_switch.step, main-board.kicad_pcb, main-board.kicad_sch]
2024-08-06 Solves the 4 batteries problem
    [4mm Panel Mount Banana Socket.stl, DPDT.step, main-board.kicad_pcb, main-board.kicad_sch]
2024-08-09 Save changes
    [main-board.kicad_pcb, main-board.kicad_sch]
2024-08-11 Improves components displacement
    [main-board.kicad_pcb]
2024-08-15 Continues placement process
    [main-board.kicad_pcb, main-board.kicad_sch]
2024-08-15 Finishes Component displacement
    [main-board.kicad_pcb, main-board.kicad_sch]
2024-08-15 Done Routing with DRC 0 Errors and 0 Warnings
    [main-board.kicad_pcb, main-board.kicad_sch]
2024-08-15 Adds upper ground plane and via stitches the board
    [main-board.kicad_pcb]
2024-08-16 Modifies auxiliary boards
    [amplifiers-B_Cu.gbr, amplifiers-B_Mask.gbr, amplifiers-B_Paste.gbr, amplifiers-B_Silkscreen.gbr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]
2024-08-16 Finishes the main board
    [main-board-B_Cu.gbr, main-board-B_Mask.gbr, main-board-B_Paste.gbr, main-board-B_Silkscreen.gbr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]
2024-08-16 Adds the fabrication zip files submited to JLC PCB
2024-08-17 Adds the orginal paper on which the board was based
2024-08-17 add images of the main board
2024-08-22 Changes the version from 0.1 to 1.0
    [amplifiers.kicad_pcb, main-board.kicad_pcb, tension-multiplier.kicad_pcb]
2024-08-25 Adds real photos of the board
